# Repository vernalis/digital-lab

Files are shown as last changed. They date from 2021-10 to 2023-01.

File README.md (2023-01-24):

# Vernalis Digital Lab

This repository contains programs for controlling laboratory operations and collecting experimental data. Published by [Vernalis Research][vr].

## Logging Thermocouple

A Raspberry Pi based thermocouple that logs datapoints to a csv file.

[Full Details][thermo]

## Inline Detector

A Raspberry Pi based inline detector, using an Adafruit AS7341 sensor. Allowing detection of slugs within a flow chemistry system, through differing visible light absorbance.

[Full Details][inline]

[vr]: https://www.vernalis.com/
[thermo]: Logging%20Thermocouple
[inline]: Inline%20Detector

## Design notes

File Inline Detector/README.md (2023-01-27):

# Raspberry Pi / Adafruit AS7341 Based Inline Detector

[][paper]


## Overview

A Raspberry Pi based inline detector, using an Adafruit AS7341 sensor. Allowing detection of slugs within a flow chemistry system, through differing visible light absorbance.

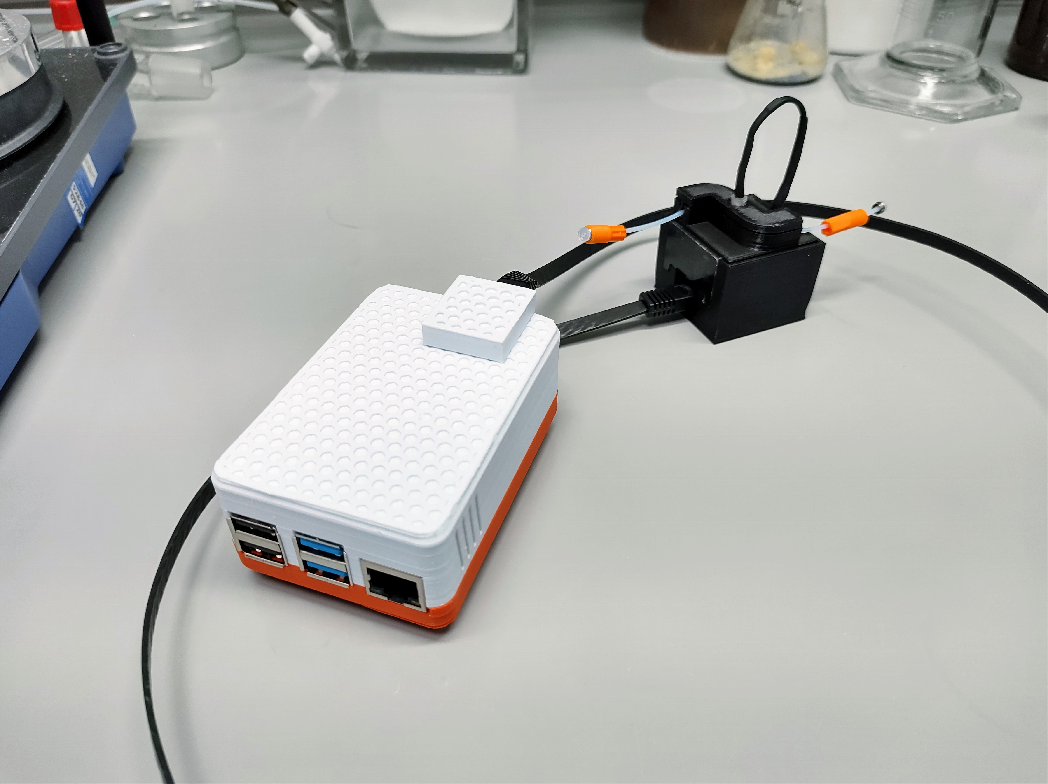
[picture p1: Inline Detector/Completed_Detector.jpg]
Pi_Detector
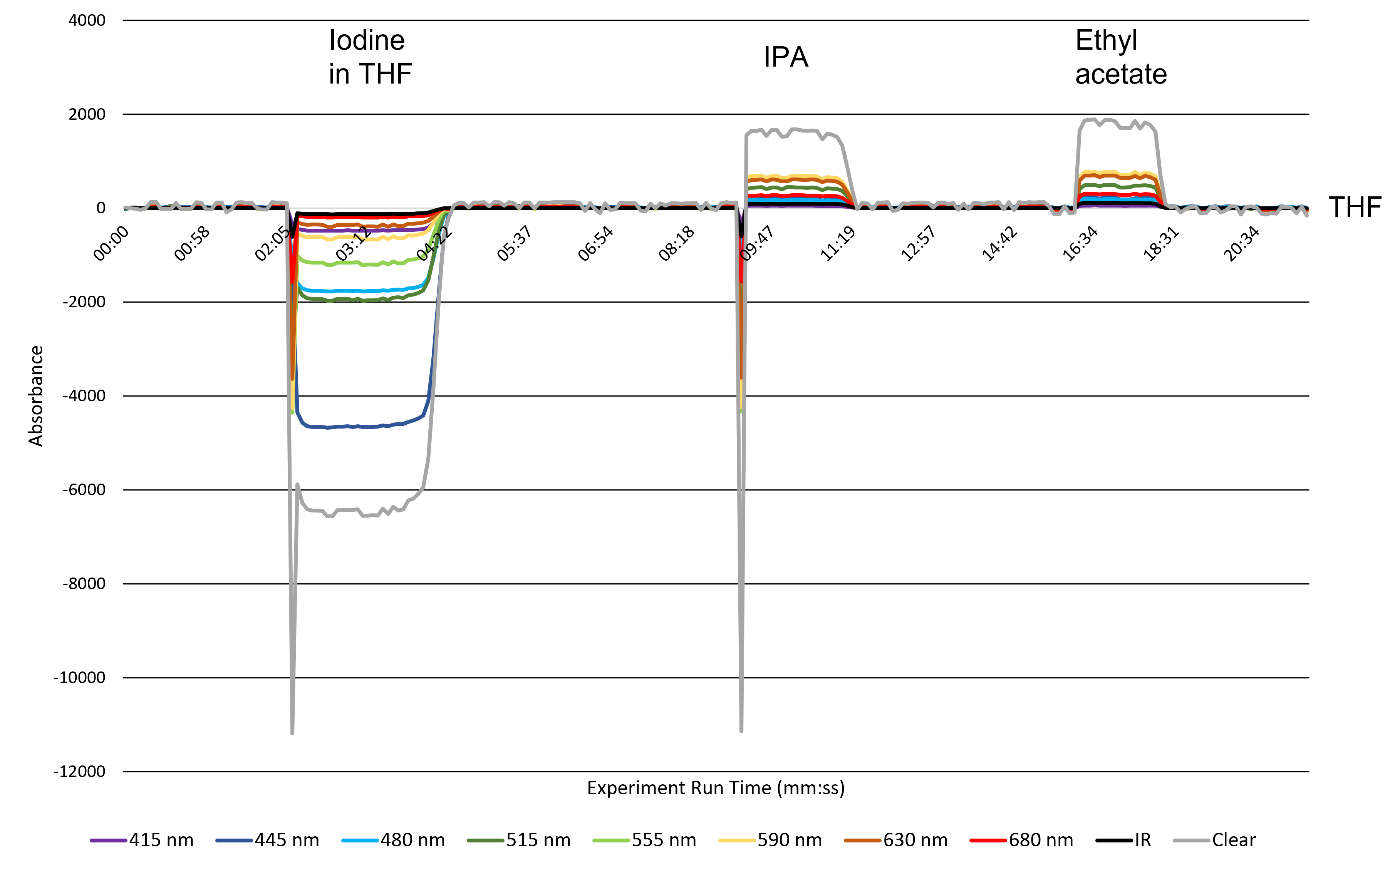
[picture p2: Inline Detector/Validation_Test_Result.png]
Graph_Output
|||
| --- | --- |
|The completed device - Raspberry Pi and detector shown|Graphical output from the detector|

[overview_img]: Completed_Detector.jpg
[graph_img]: Validation_Test_Result.png

## Publication

Details about the design and development of the device can be found in the accompanying paper. A step-by-step guide to building your own is given in the supplementary information.

[Paper][Paper] | [Supplementary Information][si]

If you have used this project as a resource in your research, please cite:

>Maddox D, Davidson JEP, Guetzoyan L, Walmsley L. Development of a Low-Cost Multi-Wavelength Inline Detector for Slug Detection in Continuous Flow. ChemRxiv. Cambridge: Cambridge Open Engage; 2023;  This content is a preprint and has not been peer-reviewed. DOI: [10.26434/chemrxiv-2023-r52zg][paper]

[paper]: https://doi.org/10.26434/chemrxiv-2023-r52zg
[si]: https://chemrxiv.org/engage/api-gateway/chemrxiv/assets/orp/resource/item/63d144546bc5cab0271aab7a/original/supplementary-information.pdf

## Bill of Materials

The following components are required to construct our design. The supplier we used is provided, however parts should be available from alternative suppliers too.

| Name | Catalogue Number | Supplier | Quantity | Total Price (£) |
| ------ | ------ | ------ | ------ | ------ |
| Raspberry Pi 4 Model B | SC0192 | Thepihut.com | 1 | 40.00 |
| 32 Gb MicroSD Card | SD-32GB | Thepihut.com | 1 | 8.00 |
| Adafruit AS7341 10-Channel Light / Color Sensor Breakout (STEMMA QT / Qwiic) | ADA4698 | Thepihut.com | 1 | 15.60 |
| 5mm White LED (forward voltage 3.4V, forward current 30mA) | Components within ELEGOO Upgraded Electronics Fun Kit (ASIN: B01LZRV539) | Amazon.co.uk | 1 | 16.99 |
| NPN Transistor (PN2222) |Components within ELEGOO Upgraded Electronics Fun Kit (ASIN: B01LZRV539)| Amazon.co.uk | 1 | N/A |
| 10 kΩ Resistor |Components within ELEGOO Upgraded Electronics Fun Kit (ASIN: B01LZRV539)| Amazon.co.uk | 2 | N/A |
| 1 kΩ Resistor |Components within ELEGOO Upgraded Electronics Fun Kit (ASIN: B01LZRV539)| Amazon.co.uk | 1 | N/A |
| Sparkfun RJ45 8-Pin Connector | PRT-00643 | Pimoroni.com | 2 | 3.00 |
| Sparkfun RJ45 Breakout | BOB-00716 | Pimoroni.com | 2 | 2.40 |
| 2x20 pin Female GPIO Header for Raspberry Pi| COM0001 |Pimoroni.com | 1 | 1.50 |
| Custom PCB for detector module (price for minimum order of 3 boards shown) | HRKGEPJB (<https://aisler.net/p/HRKGEPJB>) | Aisler.net | 1 | 6.17 |
| Custom PCB for Raspberry Pi HAT (price for minimum order of 3 boards shown) | QVZTMZVR (<https://aisler.net/p/QVZTMZVR>) | Aisler.net |1 | 7.55 |
| PLA Filament for detector module | 832-0264 | uk.rs-online.com/web | 2.7 p/g (prorated price), 37 g used | 1.00 |
| PP Filament for Raspberry Pi case feet | 174-0057 | uk.rs-online.com/web | 5.6 p/g (prorated price), 1 g used | 0.06 |
| PETG Filament for Raspberry Pi case | 190-1962 | uk.rs-online.com/web | 3.5 p/g (prorated price), 53 g used | 1.86 |
| Low profile (flat) LAN cable, 1m | Widely available, e.g. ASIN: B0B6WC6MRB | Amazon.co.uk | 1 | 2.00 |
| 1/16th inch o/d PTFE tubing, with ¼-28” connection at either end | Various suppliers | Various suppliers | Approx. 15cm required | Cost negligible |
|||| Combined Total | £106.13 |

## Repository Contents

This repository contains the following assets to enable reproduction of the device:

* **Original publication** - full documentation for the device is provided within the paper and supplementary information
* **3D Printed Parts** - .stl files for both the detector and Raspberry Pi housing
* **PCB Gerber Files** - to allow manufacture of custom PCBs with alternative suppliers
* **Code** - Python code used to operate the device (inline_detector.py) and a bash script to automate initial configuration (setup-script.sh)

### 3D Printer .stl Files

Files are separated into two folders - components for the Raspberry Pi case, and components for the detector housing.

The Raspberry Pi case is a modified version of [a publicly available Raspberry Pi 4 case](https://www.thingiverse.com/thing:3723561), modified to accommodate the custom HAT designed for this project.  

All Pi case components were printed in PETG due to the higher thermal tolerance, apart from the legs - which were printed in PP due to the higher solvent resistance.

The detector housing parts were all printed in PLA. Take care to print interlocking parts in the same orientation on the print bed to ensure a good fit.

See Supplementary Information section S4 for further details, such as printer settings.

### PCB Gerber Files

Zipped Gerber files are provided to allow manufacture of the custom PCBs at a supplier of your choice.

Alternatively, for convenience, use the following links to use the same supplier as we did. After registration, simply import the designs into your sandbox and order. A minimum order quantity of 3 is required, however the price is minimal.

[HAT PCB](https://aisler.net/p/QVZTMZVR)

[Detector PCB](https://aisler.net/p/HRKGEPJB)

See Supplementary Information section S3 for further details on circuit design. See Supplementary Information section S5 for PCB assembly.

**Note:** The HAT PCB available at publication has undergone a minor revision to the board shown in the publication. This revision decreases the board size by ~1.5mm, allowing compatibility with the Raspberry Pi Zero platform.

### Raspberry Pi Configuration and Operation

#### Configuration

A Raspberry Pi running Raspberry Pi OS Bullseye was used in combination with the following python libraries:

* CircuitPython (Blinka) by Adafruit for interfacing with their products
* adafruit-circuitpython-as7341 for the sensor device itself
* matplotlib for graphical representation of the sensor data
* pandas for data processing

The device was interfaced with predominantly via VNC to allow a familiar GUI experience.

Use the following commands in the Raspberry Pi terminal to download and run an automated configuration script to install all required libraries and the inline detector code itself in one simple process.

~~~bash
wget https://raw.githubusercontent.com/vernalis/digital-lab/main/Inline%20Detector/Code/setup-script.sh
chmod u+x setup-script.sh
./setup-script.sh
~~~

See Supplementary Information section S6.1 for a full step-by-step guide to the configuration process.

#### Operation

Once configured, operating the Raspberry Pi through VNC to allow a graphical interface, initiate the code by opening a terminal window and enter the command:

~~~bash
python inline_detector.py
~~~

After 3 initial baseline readings a graphical output of the sensor data is shown. This then updates every 2.5s with the next datapoint. Data is saved in a .csv file at each update.

At the end of the experiment, closing the window will terminate the code, saving a .png of the graph to the same folder as the .csv files.

See Supplementary Information section S6.2 for full details.

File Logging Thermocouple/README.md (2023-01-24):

# Raspberry Pi Based Logging Thermocouple

[][paper]


## Publication

Detailed information about the design and testing of these files is available in the accompanying paper:

[Paper][paper] | [Supplementary Information][si]

If you have used this project as a resource in your research, please cite:

> David Lee Walmsley, Stephen Hilton, Emilie Sellier, Matthew Penny, Daniel Maddox (2021) “Control and Monitoring of Temperature in 3D-Printed Circular Disk Reactors for Continuous Flow Photochemistry using Raspberry Pi Based Software” ChemRxiv. DOI: [10.33774/chemrxiv-2021-cxs25][paper]

[paper]: https://doi.org/10.33774/chemrxiv-2021-cxs25
[si]: https://chemrxiv.org/engage/api-gateway/chemrxiv/assets/orp/resource/item/617fc58581c4fc77f2e8b692/original/control-and-monitoring-of-temperature-in-3d-printed-circular-disk-reactors-for-continuous-flow-photochemistry-using-raspberry-pi-based-software.pdf

## Assembly Instructions

### Bill Of Materials

| Description | Product Number | Source | Price (£) |
| ------ | ------ | ------ | ------ |
| Raspberry Pi 4 Model B 2Gb | SC0193 | thepihut.com | 33.90 |
| Official UK Raspberry Pi 4 Power Supply (5.1V 3A) | SC0212 | thepihut.com | 7.50 |
| Raspbian Preinstalled 16GB Micro SD Card [Discontinued] | SC0267 | thepihut.com | 8.00 |
| Thermocouple Amplifier MAX31855 breakout board | ADA269 | thepihut.com | 13.00 |
| Thermocouple Type-K Glass Braid Insulated Stainless Steel Tip | ADA3245 | thepihut.com | 8.70 |
| RGB LCD Shield Kit w/ 16x2 Character Display | ADA716 | thepihut.com | 20.80 |
| 3D Printing Filament Made in Germany 1.75 mm 2.85 mm PLA PETG HIPS 15 Colours 1 kg Spool or Refill | 8719689844059 | amazon.co.uk | (24.88/ kg, 71 g used) 1.77 |
| **Total** |  |  | **(116.78) 93.67** |

A modified version of [a publicly available Raspberry Pi 4 case](https://www.thingiverse.com/thing:3723561) was designed to accommodate RGB LCD shield (ADA716) – allowing headless operation of the device and containment of all components. STL files and further instructions for this modified case are available in the [Vernalis 3D-printing Files Repository][case]. This was printed in PETG filament to provide good temperature resilience during operation even during high CPU usage.

[case]: https://github.com/vernalis/3Dprint_files

### Assembly

Raspberry Pi 4 containing 16Gb SD card (with operating system pre-installed) was fitted into the base of the case.

Thermocouple amplifier (ADA269) interfaces using SPI and was connected to 3V (Vin), Ground (Gnd), GPIO 9 (Do/MISO), GPIO 11 (Clk) and GPIO 5 (CS). Type-K class thermocouple (ADA3245) was connected to positive and negative terminals, noting correct polarity [ref][ADA269]. Thermocouple threaded through side port included in upper portion of case.

RGB LCD Shield (ADA716) was constructed according to supplier instructions [[ref][ADA716]]. The screen and buttons primarily interface using I2C, with the reset button operating as an independent switch monitored on a separate GPIO pin. Shield was connected to 5V, Ground, GPIO 2 (Data/SDA), GPIO 3 (Clock/SCL) and GPIO 17 (Reset, configured pin to be ‘pull up’). Screen was then mounted into upper portion of case using 4 screws (M2.5 nuts printed into the casing). Case could then be snapped together closed.

Fritzing and circuit diagrams follow below:

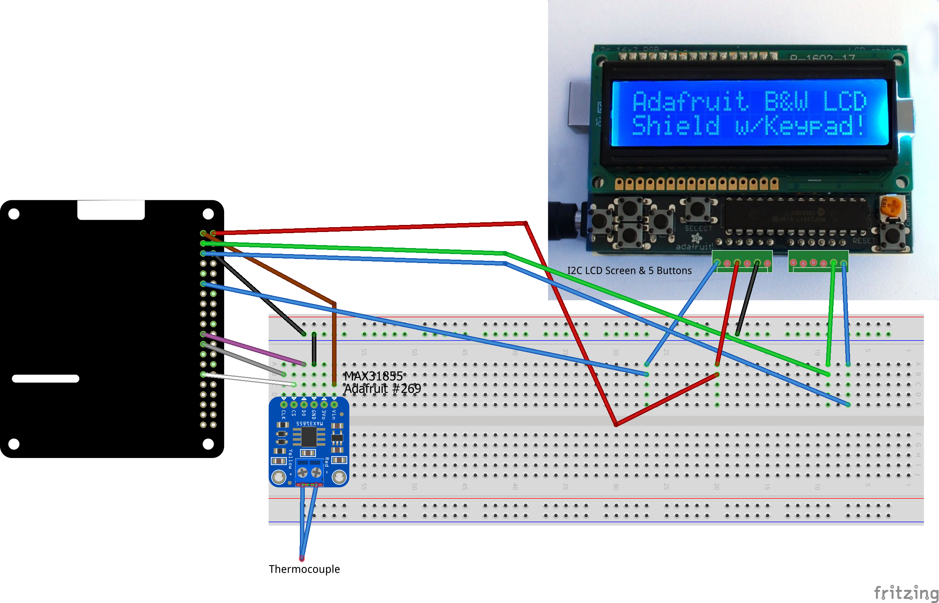
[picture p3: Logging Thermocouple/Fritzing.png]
Fritzing_Diagram


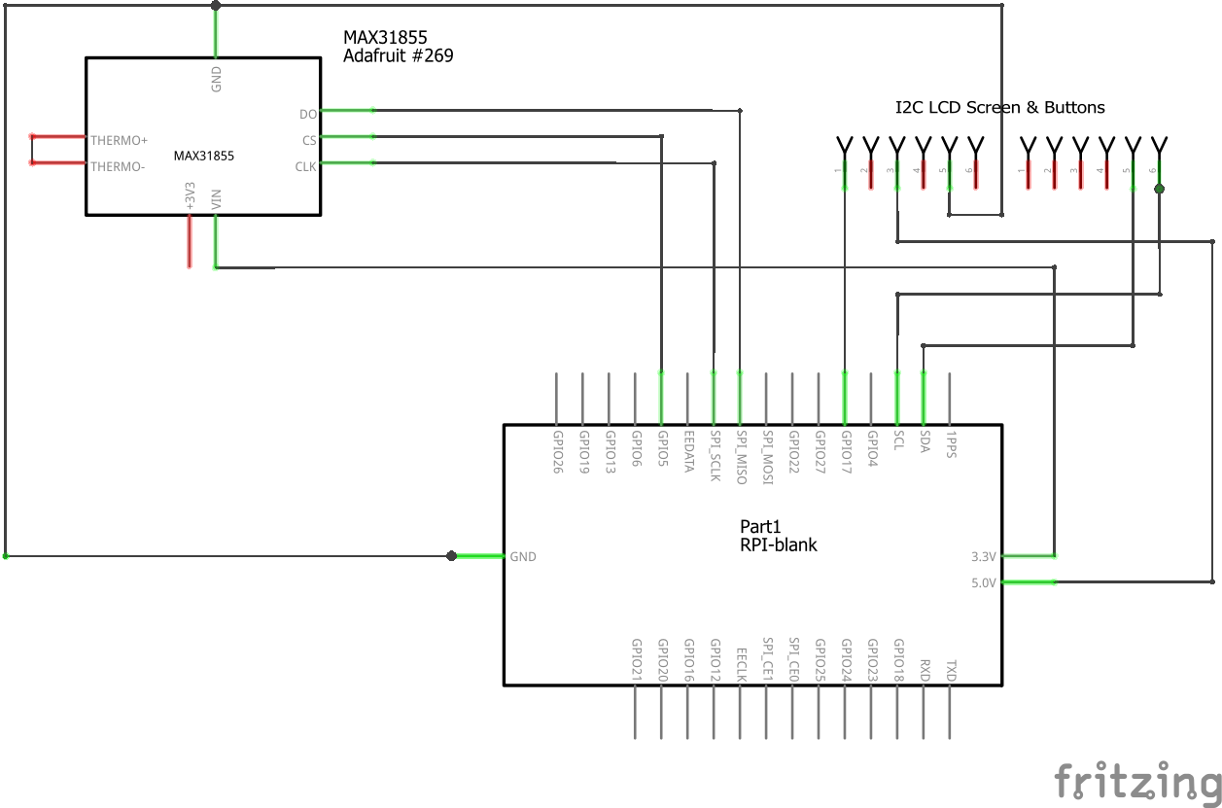
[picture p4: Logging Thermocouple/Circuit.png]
Circuit_Diagram


[circuit]: Circuit.png
[fritzing]: Fritzing.png
[ADA269]: https://learn.adafruit.com/thermocouple/overview
[ADA716]: https://learn.adafruit.com/rgb-lcd-shield/overview

## Code & Usage

Datalogging code written and tested in Python 3.7.3 using Thonny IDE. Thermocouple interface code based on that supplied by manufacturer [[ref][ADA269]]. Screen I2C interface code based on that supplied by manufacturer [[ref][ADA716]].

By default the script will output a CSV to the user folder, however can also be configured to output to a defined location by either of two methods. First, by providing the path as a command line argument:

```bash
python logging_thermocouple.py /path/to/output/folder/
```

Or secondly by setting an environment variable:

```bash
export VER_THERM_LOG=/path/to/output/folder
python logging_thermocouple.py
```

Once started, the code will log a temperature every 15 seconds to a csv file in a pre-defined file location and update the LCD screen accordingly.
To prevent log file corruption, press and hold the reset button to ‘break’ and stop the code loop.

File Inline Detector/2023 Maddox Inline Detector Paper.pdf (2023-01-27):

## Development of a Low-Cost Multi-Wavelength Inline Detector for Slug Detection in Continuous Flow

Daniel Maddox†*, James E. P. Davidson†, Lucie Guetzoyan† and Lee Walmsley†

†Vernalis Research, Granta Park, Great Abington, Cambridge, Cambridgeshire CB21 6GB, UK

Herein we describe our expansion upon previously published low-cost inline detectors. Using an Adafruit AS7341 10-channel light/colour sensor, a Raspberry Pi, and a white LED we were able to simultaneously monitor infrared and multiple visible spectrum absorption wavelengths. This allowed even challenging colourless slugs within a colourless carrier solvent to be detected and characterised as they progressed through a flow reactor. The sensor data is displayed in graphical form in real-time and stored on the device for reference afterwards.

In this publication we provide details on the design and development of a Raspberry Pi based, low-cost inline detector suitable for use with flow chemistry systems (Figure 1).

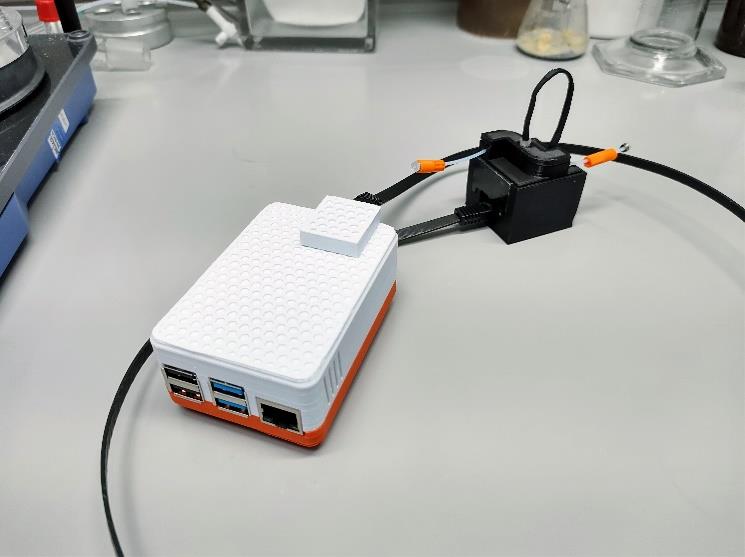
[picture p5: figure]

Flow chemistry enables reactions to be performed as a continuous process with precise control of reaction conditions such as temperature, pressure, and stoichiometry. [1]
Flow reactions can be performed in two regimes – continuous or slug flow. In continuous flow the entire fluidic system is filled with reagents, intermediate or formed product. Conversely in slug flow much of the fluidic system is filled with carrier solvent, small discrete reaction slugs then flow through the system (Figure 2, A). Although slug flow reactions are being performed on a much smaller reaction scale, on a microfluidic scale the same reaction is performed. This means at identical positions within the flow reactor an identical profile is observed in both the slug and continuous flow regime. This linear scalability makes slug flow chemistry ideal for library synthesis in flow.

Two critical considerations when performing slug flow chemistry is the timing and profile of the slug. Knowing to a high degree of accuracy where a reaction slug is within a fluidic system that is likely 10 or more times the volume of the reaction slug is crucial to enable effective collection of the product solution. This becomes even more apparent when two reactant slugs need to meet at a t-mixer. For a complete reaction, both slugs need to begin and end with perfect synchronicity (Figure 2, B) – where the two slugs do not overlap one reagent does not see the other, meaning no reaction can occur (Figure 2, C).

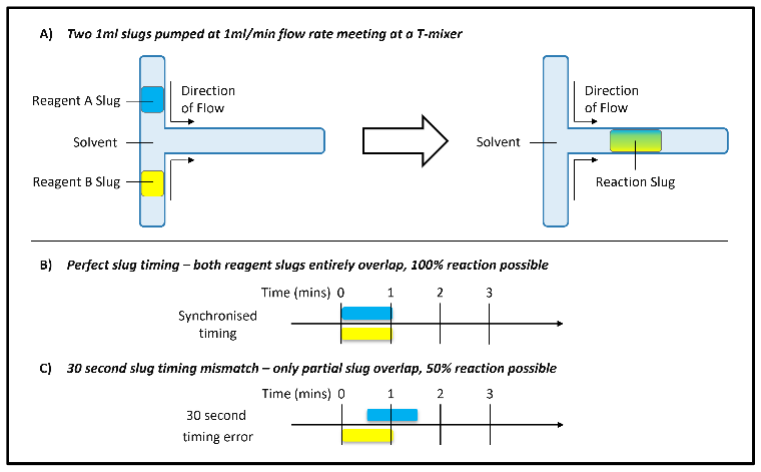
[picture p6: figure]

Prediction of slug timing within a simple tubular flow reactor can be achieved when both the flow rate and system volume are known to a high degree of accuracy, so long as the flow rate is well controlled. In more complex fluidic systems however – in particular when a solid phase reactor is present – prediction of slug timing can become more difficult to predict due to the chromatographic effect of the stationary phase reaction surface. [2]

Figure 2 - A) Representation of two reagent slugs meeting at a T-mixer. B & C) The importance of slug timing

Figure 1 - Our completed design - a low cost detector module connected to a Raspberry Pi computer

If reaction slugs are highly coloured, and see-through PTFE/PFA or similar material tubing is used then slug timing can be corroborated by eye. If either of these factors is not the case however, then inline detection is required to ‘see’ the reaction slug. Several inline detection technologies are commercially available including inline flow NMR, MS, IR or UV.

[3 - 4] All of
these commercial examples however are significantly priced and have a sizeable footprint to accommodate within a fume cupboard that likely already contains a large amount of equipment associated with the flow reactor itself. As a result, multiple groups have reported their efforts to overcome these issues, creating low-cost inline detectors relying on the absorbance of visible spectrum light. [5 - 6]

Whilst elegant and likely to generate high quality and sensitive data thanks to the reference measurement being taken, the resultant complex optical setup using a beam-splitter cube and optical fibres of the detector published by Glotz & Kappe [5] makes replication of
the | literature | challenging | without | sufficient
engineering expertise.

The later publication from Höving et al.

[6] was the
basis of a much simpler design. In the Höving et al. publication, the flow reactor tube was sandwiched between a coloured LED (Light Emitting Diode) and LDR (Light Dependent Resistor) and held together in a specially designed 3D printed housing. The simplicity of this design made it a much more tangible prospect for us to be able to reproduce. The reliance of the design however, on a single wavelength LED, and typically low sensitivity LDR, made us question if further enhancements could be made to increase the applicability.

With the rise of single board computers such as the Raspberry Pi and Arduino Uno a market has emerged for a wide range of sensors that can easily be incorporated into these systems. For this application, the Adafruit AS7341 sensor looked ideal. [7] The sensor measures light across 10 wavelength ‘channels’ (IR, 8 visible spectrum wavelengths, and a ‘clear’ channel that covers that entire spectrum) and can be interfaced with easily using I

2C (Inter-Integrated
Circuit). If a white LED was used to irradiate the reactor pipe, then the absorbance of the fluid within the pipe could be determined at multiple wavelengths simultaneously – providing richer data than the previously published inline detectors at a similar low cost.

Measuring absorbance across a wide range of wavelengths would also negate the need to optimise the detector for the substrate you wish to measure. Comparing the absorbance ‘fingerprints’ of two apparently colourless substances could enable easy identification of colourless slugs within a colourless carrier solvent.

Design and Development

Using the “Version B” flow cell design from the Höving et al. publication [6] as a starting point, an initial prototype detector housing was designed in Tinkercad.[8] Although only 2.6 x 1.8 cm in size, the Adafruit AS7341 sensor board is significantly larger than an LDR as used in the previous publication. As a result, modifications were required to encase the

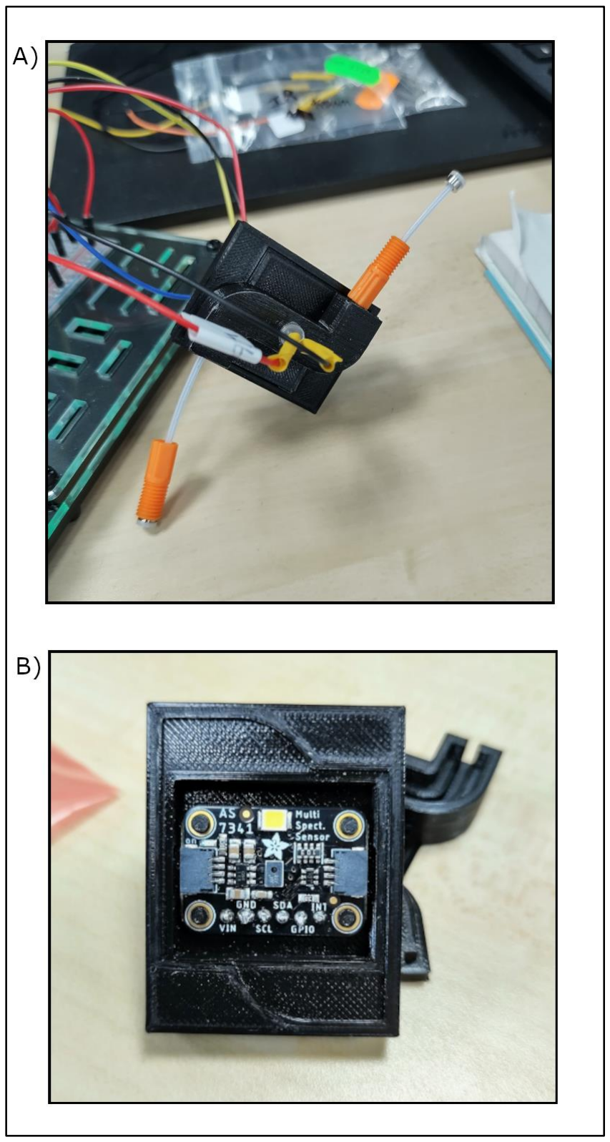
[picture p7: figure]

Figure 3 - A) Assembled prototype inline detector B) Sensor within prototype detector module

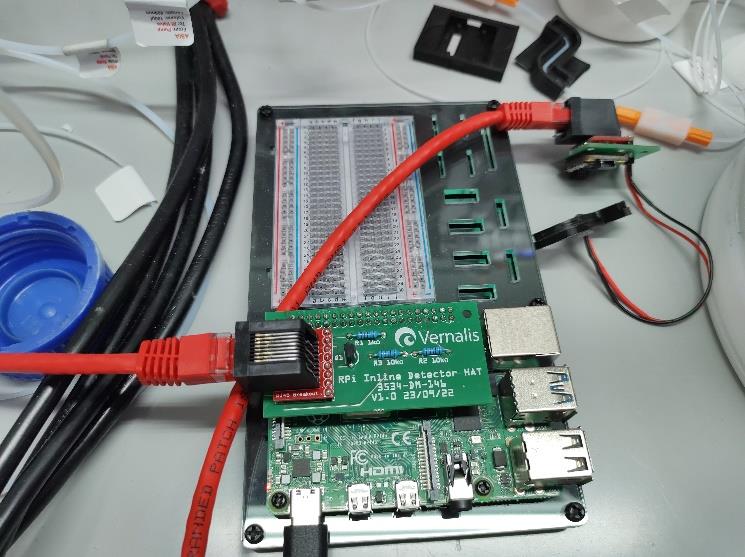
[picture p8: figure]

larger Adafruit AS7341 sensor board to create a light-proof box, whilst exposing the sensor pins to allow circuit prototyping with the Raspberry Pi and a breadboard (Figure 3).

To complete the prototype device a white LED was also controlled by the Raspberry Pi, using PWM (Pulse Width Modulation) to optionally control brightness of the LED, allowing the effect of varying irradiation brightness to be tested.

Initial experiments using this prototype device confirmed our hopes. Using the example code provided by Adafruit [7] and pumping test solutions through the flow cell using a hand operated syringe; THF, IPA (isopropyl alcohol) and ethyl acetate showed differences in absorbance, despite all being colourless liquids to the human eye.

To transform the prototype into a useable device that could be housed and operated in a laboratory fume cupboard two major improvements needed to be made: the fragile breadboard prototype circuitry needed to be rigidified and then protected from potential solvent splashes etc, and a better representation of the sensor data also needed to be created rather than using the Adafruit example code.

To consolidate and rigidify the circuitry bespoke printed circuit boards were designed using circuit design software tool Fritzing and then fabricated at a low volume PCB manufacturer, Aisler. A design strategy commonly employed in the single board computer arena was used – a Pi HAT (Hardware Attached on Top) circuit board was designed to contain all the control electronics in an easily attachable/detachable board. A second smaller circuit board was designed for the detector and LED.

On both boards was also included an RJ45 (ethernet) port. An ethernet cable was chosen to consolidate the 6 wires required to power the LED and communicate with the sensor into a single cable (leaving two of the eight wires unused). The choice was made to use a ubiquitous, easily interchangeable cable so that any cable of suitable length could be selected as required dependent on location. This design then allows the detector and Raspberry Pi to be located any distance apart by simply choosing a longer or shorter ethernet cable (Figure 4).

The initial proof-of-concept code supplied by Adafruit displays the sensor wavelength readings in a histogram form, refreshing each time sensor values are read. To allow us to see changes in absorption over time, and thus identify when slugs are passing the detector, the data needed to be represented as a line graph – plotting sensor readings versus time (Figure 6). This was achieved using the python programming language: using the “pandas” module for tabular data storage and “matplotlib” to output the data in a graphical form. In addition to displaying the plot in real-time, the tabulated data as a .csv file and a .png image of the graph are also stored.

Further testing of the device was carried out to determine the best operation protocol. It was found slugs were much easier to visualise graphically if the sensor channel data is baselined to the absorbance of the system solvent (see Supplementary Information, Figure S20). This then results in a clear positive or negative peak in the trace when a slug is passing the detector. LED brightness was also tested, and full power was found to give the best signal to noise ratio (the LED is not too bright to cause saturation of the detector).

Finally, we needed to provide a secure and protective housing for the new detector circuit board and separately the Raspberry Pi computer. The initial prototype 3D printed sensor housing was modified further to accommodate the RJ45 connector now included. The sensor device is an approximately 4.5 x 4.5 x 4.5 cm cube – still a very small footprint and thus very portable, allowing positioning wherever required in a fluidic system (Figure 5). For the Raspberry Pi

Figure 4 - Custom circuit boards consolidate device electronics, using an ethernet cable to connect the sensor board to the Raspberry Pi HAT

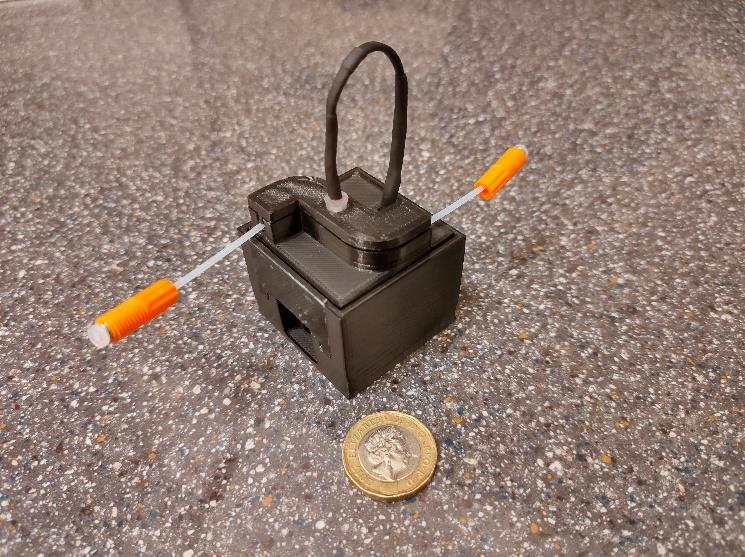
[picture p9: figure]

housing, a suitable case available on the Thingiverse was chosen. [9] Minor modifications were made to accommodate the RJ45 connector we introduced, which stands taller than most Pi HAT devices.

With construction of the final design complete we carried out a more thorough validation test using our Syrris Asia flow chemistry system. Running THF as the system solvent we injected sequential slugs of dilute iodine in THF (as a coloured, positive control) followed by IPA and then ethyl acetate. All slugs could be clearly visualised as distinctly different to the THF system solvent – confirming the device works as anticipated (Figure 6).

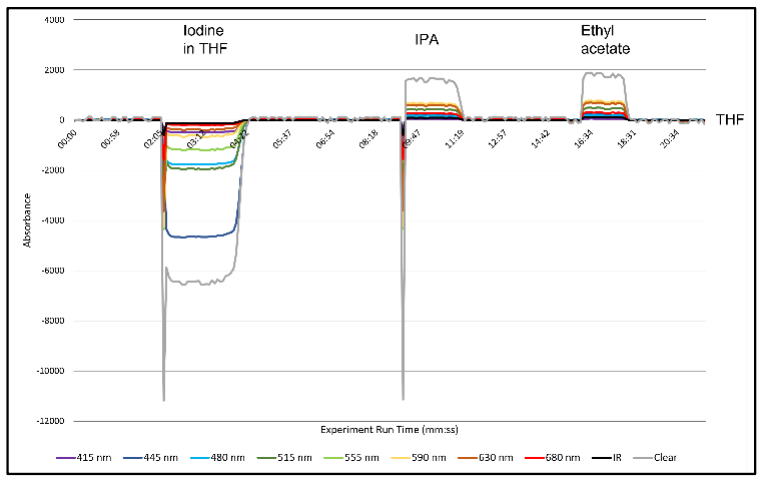
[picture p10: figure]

Conclusion

In conclusion, in this publication we report a significant enhancement on the previously published low-cost inline detector from Höving et al. [6] by changing the detector to one that can measure multiple wavelengths simultaneously and changing the irradiation source to a white LED. As a result, we were able to obtain real-time inline spectral data from a flow reactor operating in a slug flow regime, indicating when slugs pass the detector even when undetectable to the human eye.

This device enables slug timing within a flow reactor to be determined in a quick and facile manner. Furthermore, the device could be used to monitor residence time distribution within a system based on shape of the slug peak, along with perhaps estimation of reaction conversion if the optical absorbance profile of starting material and product were known.

Details to construct the device are provided in the supplementary information document, including links to purchase the printed circuit boards directly from the manufacturer we used. Source code, 3D print .stl files and circuit board Gerber files (if you wish to organise manufacture yourself) are all provided on our GitHub repository:

https://github.com/vernalis/digital-lab/tree/main/Inline%20Detector (https://github.com/vernalis/digital-lab/tree/main/Inline%20Detector)

References

[1] Plutschack, M. B. et al. The Hitchhiker’s guide to flow chemistry. Chem. Rev., 2017, 117, 11796-11893.
https://doi.org/10.1021/acs.chemrev.7b0018 3 (https://doi.org/10.1021/acs.chemrev.7b00183)
[2] Abdiaj, I. et al. End-to-end automated synthesis of C(sp³
)-enriched drug-like
molecules via Negishi coupling and novel, automated liquid-liquid extraction. J. Med. Chem.¸2023, 66, 1, 716-732. https://doi.org/10.1021/acs.jmedchem.2c016 46 (https://doi.org/10.1021/acs.jmedchem.2c01646)
[3] Rodriguez-Zubiri, M. & Felpin, F.-X. Analytical tools integrated in continuous-flow reactors: which one for what? Org. Process Res. Dev., 2022, 26, 6, 1766-1793.
https://pubs.acs.org/doi/10.1021/acs.oprd.2c 00102 (https://pubs.acs.org/doi/10.1021/acs.oprd.2c00102)
[4] https://www.uniqsis.com/paProductsDetail.aspx?ID=Flow-UV (https://www.uniqsis.com/paProductsDetail.aspx?ID=Flow-UV)
[5] Glotz, G. & Kappe, C. O. Design and construction of an open source-based photometer and its applications in flow chemistry. React. Chem. Eng., 2018, 3, 478-
486. https://doi.org/10.1039/C8RE00070K

Figure 5 - The finalised detector module. £1 coin for scale

Figure 6 - Graphical output from detector - slugs are clearly detectable versus THF baseline

[6] Höving, S., Bobers, J. & Kockmann, N. Open-source multi-purpose sensor for measurements in continuous capillary flow. J Flow Chem 12, 185–196 (2022). https://doi.org/10.1007/s41981-021-00214-w
[7] https://learn.adafruit.com/adafruit-as7341-10-channel-light-color-sensor-breakout/ (https://learn.adafruit.com/adafruit-as7341-10-channel-light-color-sensor-breakout/)
[8] https://www.tinkercad.com/3d-design
[9] https://www.thingiverse.com/thing:3723561

[*] Corresponding Author
Daniel Maddox
Vernalis Research,
Granta Park,
Great Abington,
Cambridge,
CB21 6GB
e-mail: d.maddox@vernalis.com

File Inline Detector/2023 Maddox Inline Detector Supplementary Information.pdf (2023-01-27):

# Supplementary Information

# Development of a Low-Cost Multi-Wavelength Inline Detector for Slug Detection in Continuous Flow

Daniel Maddox†*, James E. P. Davidson†, Lucie Guetzoyan† and Lee Walmsley†

†Vernalis Research, Granta Park, Great Abington, Cambridge, Cambridgeshire CB21 6GB, UK

[*] Corresponding Author
Daniel Maddox
Vernalis Research,
Granta Park,
Great Abington,
Cambridge,
CB21 6GB
e-mail: d.maddox@vernalis.com

S2

## Table of Contents

S1 - General Considerations | S3
S2 - Bill of Materials | S4
S3 - Circuit Design | S5
S3.1 - Prototype Circuit Design | S6
S3.2 - Finalised Circuit Design | S7
S3.3 - Custom Circuit Board Availability | S9
S4 - Design of 3D Printed Housings | S10
S4.1 - Detector Module Design | S10
S4.2 - Raspberry Pi Case Design | S13
S4.3 - STL File Availability | S14
S4.4 - 3D Printing Settings | S14
S5 - Assembly of Devices | S15
S5.1 - Assembly of Detector Module Circuit Board | S15
S5.2 - Assembly of Detector Module | S17
S5.3 - Assembly of HAT Circuit Board | S19
S5.4 - Assembly of Raspberry Pi Module | S20
S6 - Raspberry Pi Configuration and Operation | S21
S6.1 - Configuring Raspberry Pi for Use | S21
S6.2 - Inline Detector Operation | S22
S7 - Testing | S23
S7.1 - Initial Optimisation | S23
S7.2 - Validation of Detector | S24
S8 - References | S25

## S1 - General Considerations

Herein we provide full details of the design, assembly, and use of our inline detector.

The design consists of two major components: the detector module which houses the detector, fluidic piping (acting as the flow cell), a white LED and a RJ45 connector; and a Raspberry Pi 4 Model B which comprises of a standard Raspberry Pi as well as a custom HAT (Hardware Attached on Top) which contains the control electronics for the LED in addition to a RJ45 connector. The two devices are interconnected using an RJ45 cable. Both devices are housed in custom designed 3D-printed cases. A Raspberry Pi Zero should also be compatible, however the smaller 3D printed case has not been designed, nor has the lesser computational performance been tested.

The detector is operated using the Raspberry Pi, interfacing via a connected screen or remote desktop protocol. The supplied code plots a graph of datapoints from the detector, refreshing upon each new datapoint acquisition. The code also stores the data as a .csv file for review later, along with a .png image of the graph.

All associated files can be found on the Vernalis GitHub: https://github.com/vernalis/digital-lab/tree/main/Inline%20Detector (https://github.com/vernalis/digital-lab/tree/main/Inline%20Detector)

## S2 - Bill of Materials

The following components and materials are required to construct our design:

Item | Catalogue Number | Supplier | Quantity | Total Price (£)
Raspberry Pi 4 Model B | SC0192 | Thepihut.com | 1 | 40.00
32 Gb MicroSD Card | SD-32GB | Thepihut.com | 1 | 8.00
Adafruit AS7341 10-Channel Light / Color Sensor Breakout (STEMMA QT / Qwiic) | ADA4698 | Thepihut.com | 1 | 15.60
5mm White LED (forward voltage 3.4V, forward current 30mA) | Components within ELEGOO Upgraded Electronics Fun Kit ASIN: B01LZRV539 | Amazon.co.uk | 1 | 16.99 NPN Transistor
(PN2222) | | | 1
10 kΩ Resistor | | | 2
1 kΩ Resistor | | | 1
Sparkfun RJ45 8-Pin Connector | PRT-00643 | Pimoroni.com | 2 | 3.00
Sparkfun RJ45 Breakout | BOB-00716 | Pimoroni.com | 2 | 2.40
2x20 pin Female GPIO Header for Raspberry Pi | COM0001 | Pimoroni.com | 1 | 1.50
Custom PCB for detector module (price for minimum order of 3 boards shown) | HRKGEPJB (https://aisler.net/p/HRKGEPJB) | Aisler.net | 1 | 6.17
Custom PCB for Raspberry Pi HAT (price for minimum order of 3 boards shown) | QVZTMZVR (https://aisler.net/p/QVZTMZVR) | Aisler.net | 1 | 7.55
PLA Filament for detector module | 832-0264 | uk.rs-online.com/web | 2.7 p/g (prorated price), 37 g used | 1.00
PP Filament for Raspberry Pi case feet | 174-0057 | uk.rs-online.com/web | 5.6 p/g (prorated price), 1 g used | 0.06

PETG Filament for Raspberry Pi case | 190-1962 | uk.rs-online.com/web | 3.5 p/g (prorated price), 53 g used | 1.86
Low profile (flat) LAN cable, 1m | Widely available, e.g. ASIN: B0B6WC6MRB | Amazon.co.uk | 1 | 2.00
1/16th inch o/d PTFE tubing, with ¼-28” connection at either end | Various suppliers, approx. 15cm required, cost negligible
| | | Combined total | £106.13

Table S1 - Bill of materials

## S3 - Circuit Design

The device consists of two circuits (sensor board and LED), both are powered and controlled by the Raspberry Pi.

The sensor board is powered by 3.3V and communicates with the Pi over I²C (thus using the SDA and SCL pins). The sensor board is therefore connected to GPIO pins 2 (I²C SDA), 3(I²C SCL), a 3v3 and a ground pin.

The high-power white LED has a forward voltage greater than that provided by a standard GPIO pin (3.4V versus 3.3V). As a result, the LED must be powered by a 5V pin (with 1 kΩ resistor) and then controlled by a separate GPIO pin using an NPN transistor (via a 20 kΩ resistor) to complete the circuit. [1] To allow dimming of the LED brightness, the controlling GPIO pin uses PWM (Pulse Width Modulation) [2]
, however in our initial studies we have found 100% brightness (i.e. no PWM) gave the best signal/noise result (see S7.1). The LED circuit is thus connected to GPIO pin 13 (PWM), a 5V and a ground pin.

In the prototype circuit design all circuits were directly connected between the component and the Raspberry Pi. In the finalised design, to allow easy and customisable length of separation between the Raspberry Pi and the detector module, as well as consolidation of 6 wires into one cable, an RJ45 ethernet cable was used. Components are attached to each other via the PCB circuitry, rather than the wires depicted in the original prototype diagram.

For ease of understanding both the prototype and finalised circuits are provided in the following sections, however both are essentially identical.

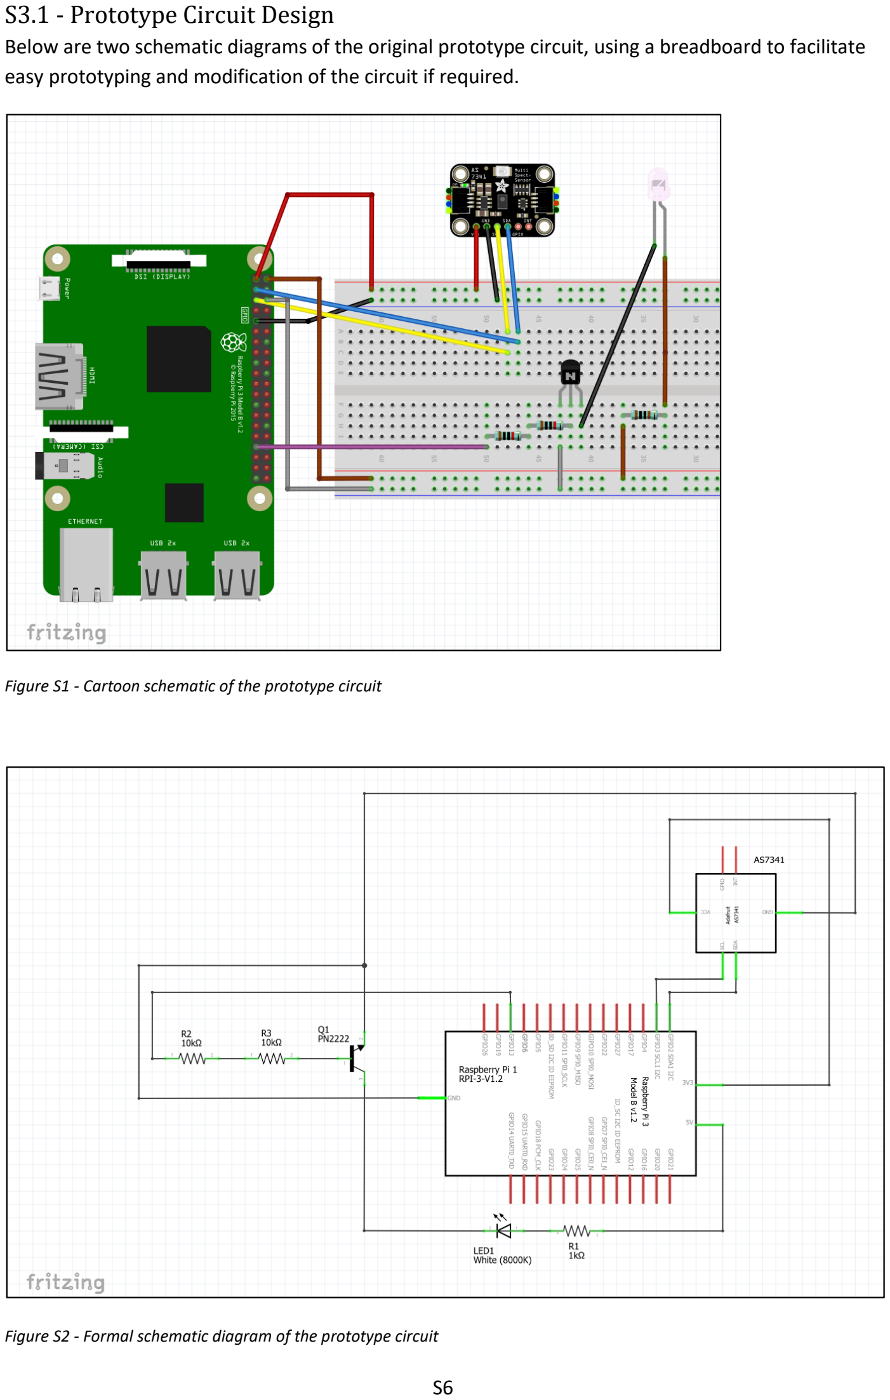
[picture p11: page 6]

### S3.1 - Prototype Circuit Design

Below are two schematic diagrams of the original prototype circuit, using a breadboard to facilitate easy prototyping and modification of the circuit if required.

Figure S1 - Cartoon schematic of the prototype circuit

Figure S2 - Formal schematic diagram of the prototype circuit

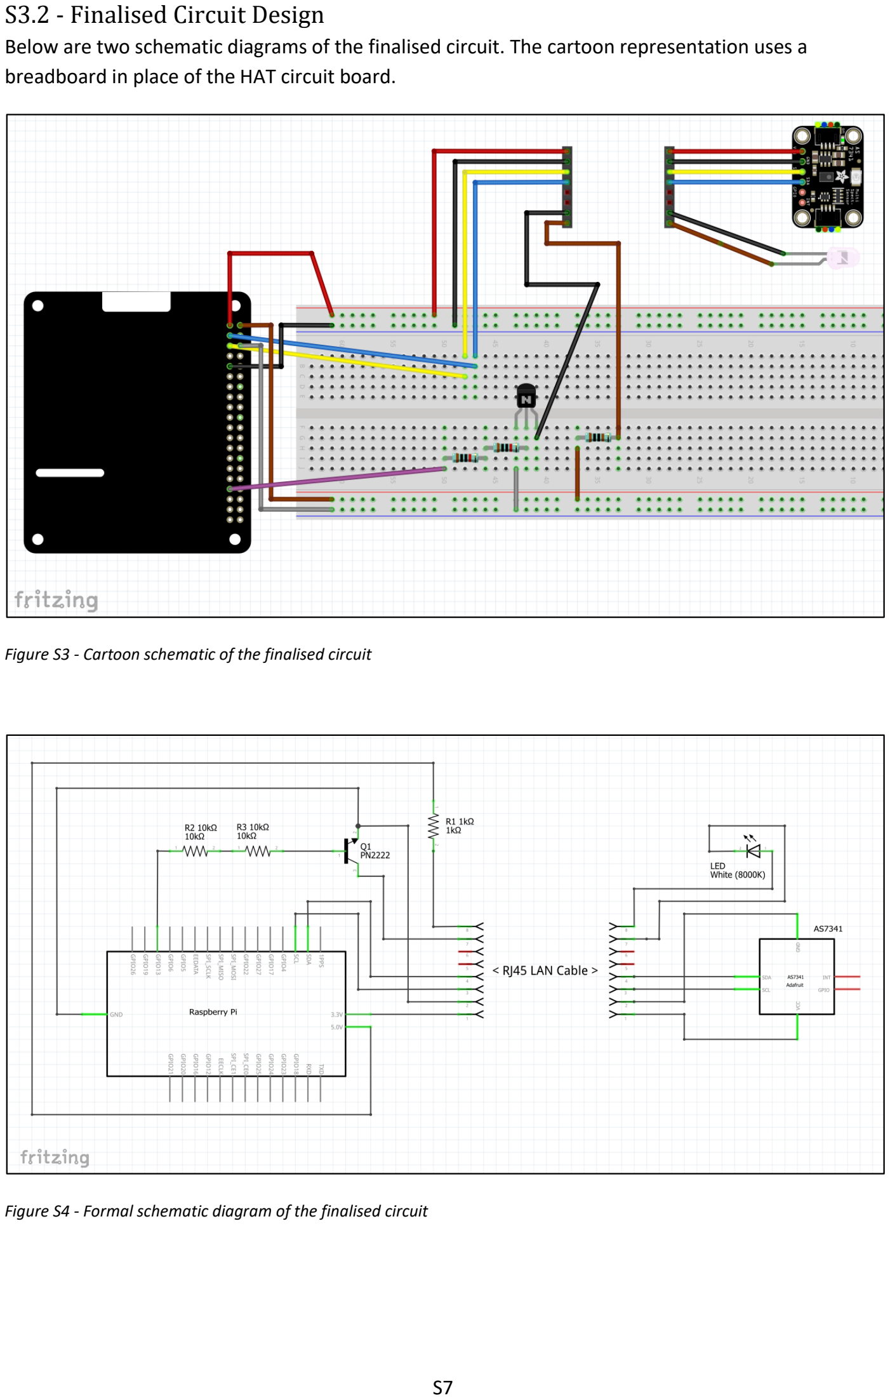
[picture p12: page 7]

### S3.2 - Finalised Circuit Design

Below are two schematic diagrams of the finalised circuit. The cartoon representation uses a breadboard in place of the HAT circuit board.

Figure S3 - Cartoon schematic of the finalised circuit

Figure S4 - Formal schematic diagram of the finalised circuit

Below are the two custom PCB designs. To keep the detector module as small as possible the sensor and LED are on one side of the board, with the RJ45 connector mounted on the underside. A female GPIO socket connector was used to enable easy attachment/detachment of the HAT to the Pi. Note: the two different colours of orange depict the two copper layers within the board. Black markings indicate silkscreen labels on the boards. The HAT is small enough to also fit a Pi Zero.

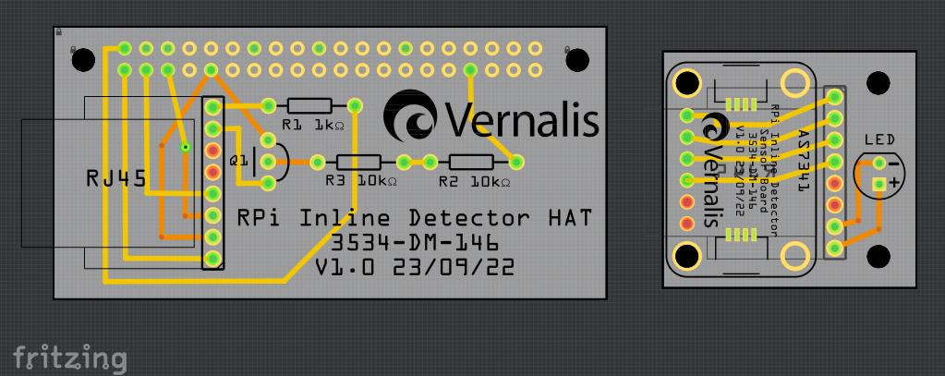
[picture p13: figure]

Figure S5 - Custom PCB designs

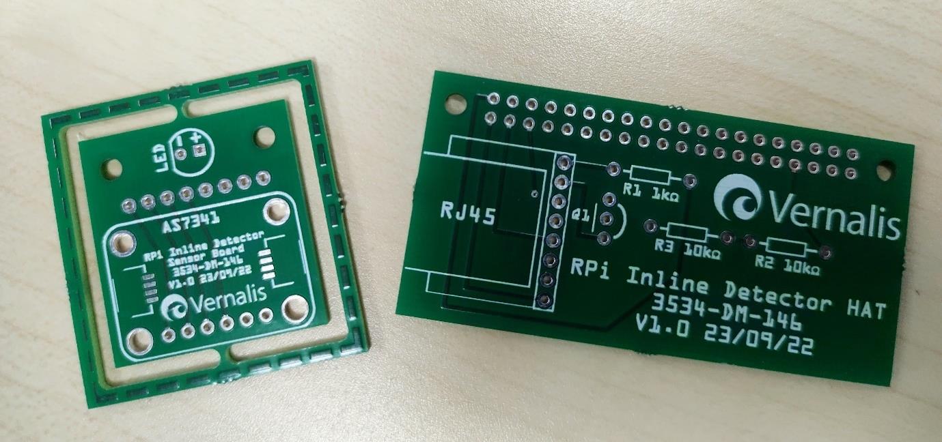
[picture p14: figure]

Figure S6 - Custom PCBs as delivered. Note - smaller detector board has manufacturing excess that requires removal

### S3.3 - Custom Circuit Board Availability

The two custom PCB designs are available to order directly from the manufacturer we used (Aisler). To order the HAT visit https://aisler.net/p/QVZTMZVR , to order the detector module board visit https://aisler.net/p/HRKGEPJB . After registration the designs can then be imported to your account and ordered. A minimum order quantity of 3 is required, however the price is minimal (see Table 1).

Alternatively, the PCB Gerber files have been uploaded to our GitHub page, allowing manufacture elsewhere - https://github.com/vernalis/digital-lab/tree/main/Inline%20Detector/PCB%20Gerber%20Files (https://github.com/vernalis/digital-lab/tree/main/Inline%20Detector/PCB%20Gerber%20Files)

Note: The HAT PCB available at publication has undergone a minor revision to the board shown above. This revision decreases the board size by ~1.5mm, allowing compatibility with the Raspberry Pi Zero platform.

See section S5 for assembly instructions.

## S4 - Design of 3D Printed Housings

All 3D design was carried out using Tinkercad – a free, web-based CAD tool.

### S4.1 - Detector Module Design

The starting point for the detector module design was the previously published “Version B” sensor housing design by Höving et al.. [3] Using the stl for this design and creating a CAD version of the Adafruit AS7341 sensor we were able to design the additional structure required to create a secure, lightproof housing for the larger sensor.

As an initial prototype, we designed a housing to simply encase the sensor (Figure S7).

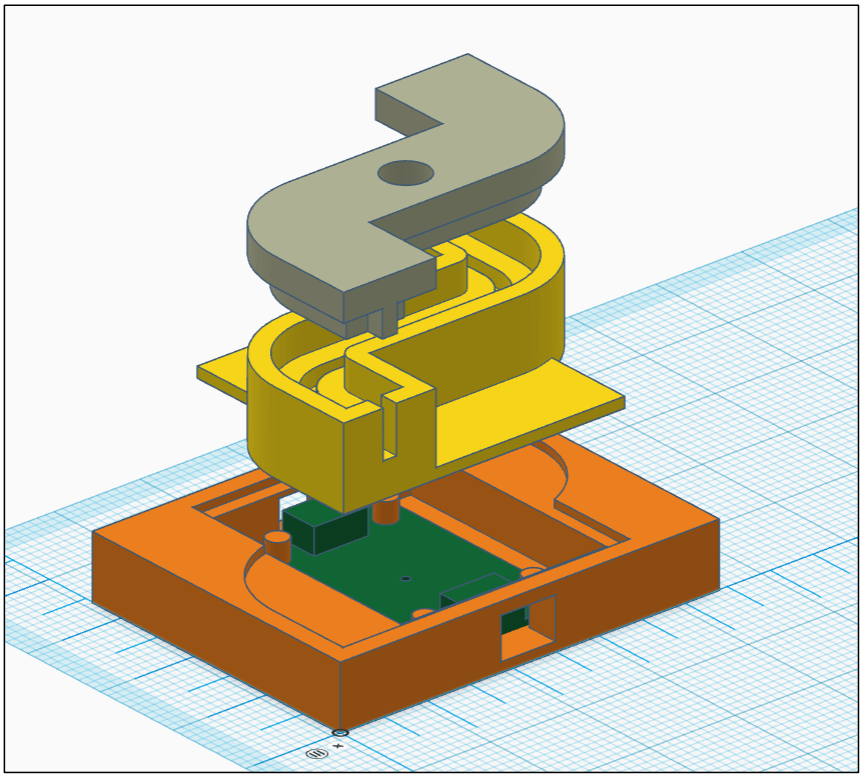
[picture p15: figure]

Figure S7 - Exploded CAD view of prototype detector module

Once initial success was confirmed and we moved to the finalised circuit, with custom circuit board and RJ45 link between the Raspberry Pi and detector module we designed a larger detector module housing incorporating the RJ45 connector and an access hole through which the LED wires could be fed (Figure S8, Figure S9).

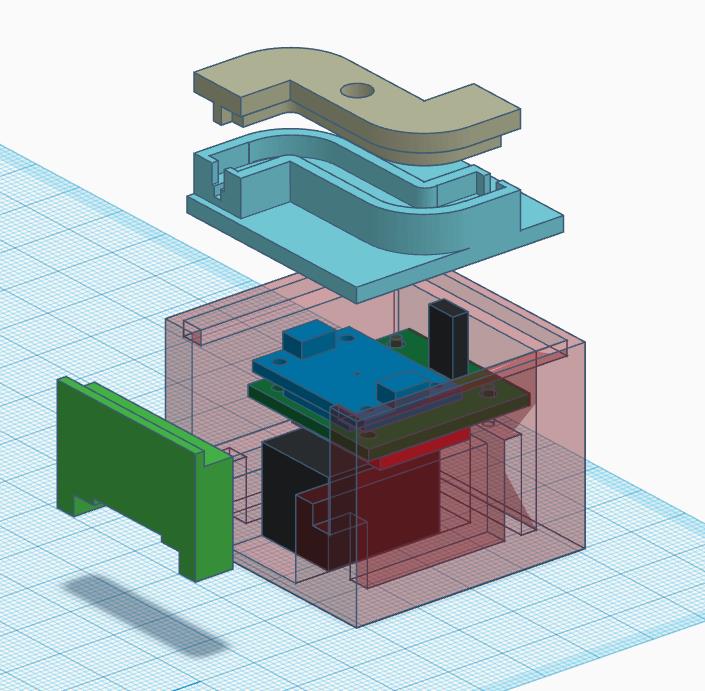
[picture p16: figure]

Figure S8 - Exploded CAD view of finalised detector module

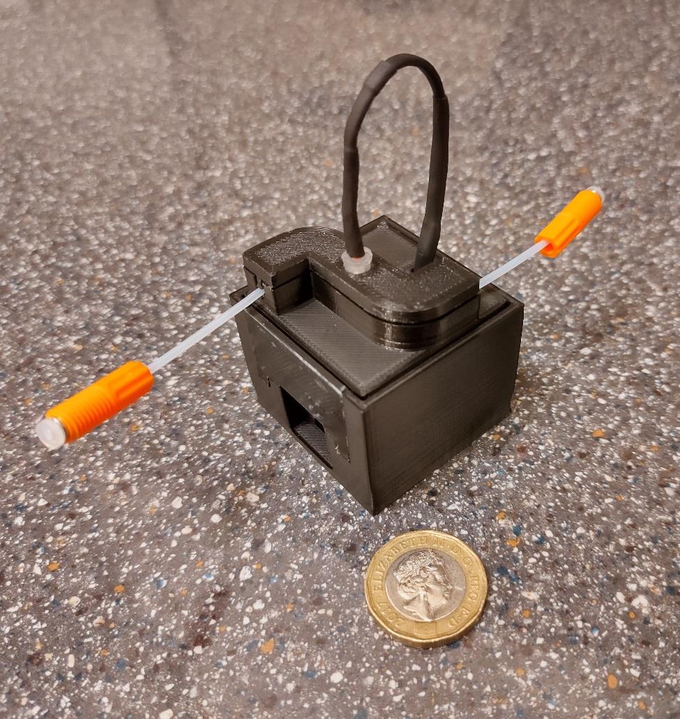
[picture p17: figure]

Figure S9 - 3D printed and fully constructed detector module

### S4.2 - Raspberry Pi Case Design

The starting point for the Raspberry Pi case design was the snap-fit design published by Malolo on the Thingiverse. [4]

The inclusion of the RJ45 connector on the custom HAT board resulted in a vertical height greater than is standard for Raspberry Pi devices. As a result, a small cut-out was made in the top surface of the case to allow the connector to stand proud. A small additional cap was then made to insert into the slot created – ensuring the RJ45 port was still protected.

In addition to this modification, to the top surface of the Pi case (and cap) was added a stippled pattern. This was for aesthetic reasons, to overcome the inconsistent patternation caused by the print bed (the case and cap are printed upside down relative to their intended orientation during use).

A further minor addition to the Malolo design was the inclusion of 4 feet to raise the bottom of the case off the fume hood floor – improving airflow, processor heat dissipation and protection from spilt solvent.

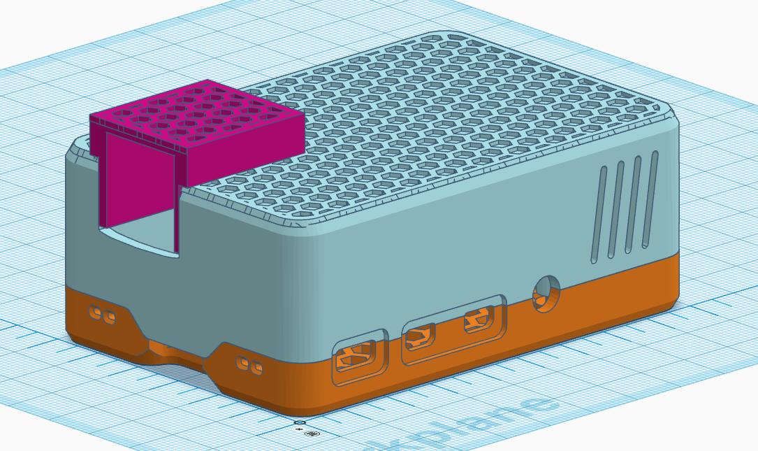
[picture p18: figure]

Figure S10 - Pi case CAD view: the base in orange, top in blue and RJ45 cap in pink. Feet are not shown.

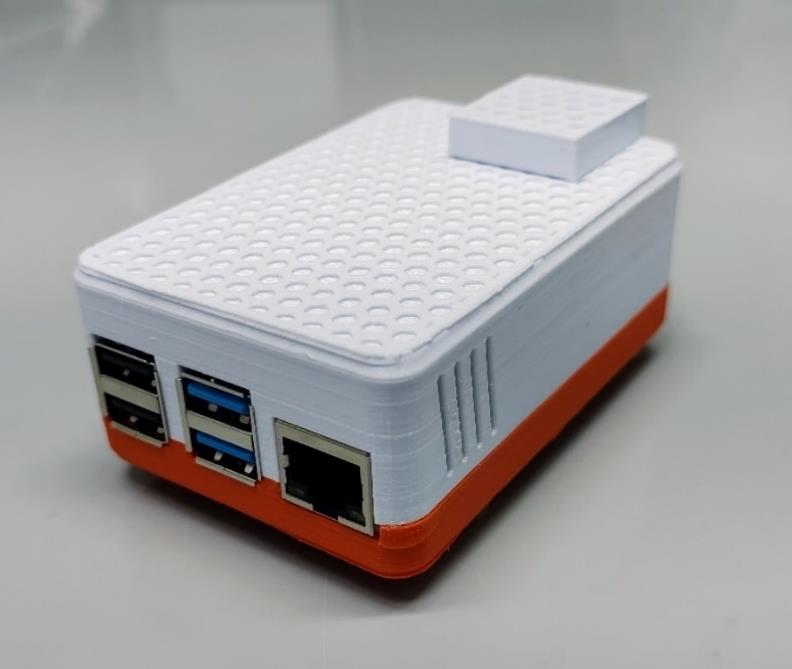
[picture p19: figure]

Figure S11 - Constructed Pi case

### S4.3 - STL File Availability

All .stl files for the finalised design are available from our GitHub page -https://github.com/vernalis/digital-lab/tree/main/Inline%20Detector/3D%20Printed%20Parts

See S4.4 for optimal printing settings and S5.2 & S5.4 for assembly instructions.

### S4.4 - 3D Printing Settings

All components were 3D printed using an Ultimaker S5, using 2.85mm filament.

The Raspberry Pi case was printed in polyethylene terephthalate glycol (PETG) due its higher tolerance to temperature – preventing any warping during use due to heat coming from the Pi’s processor.

The Pi case feet were printed in polypropylene (PP) due to its higher solvent resistance.

The detector module had no material requirements (other than being opaque), therefore polylactic acid (PLA) was used.

When printing interlocking parts (e.g. the fluidic pipe guide) these should be printed in the same orientation as each other on the print bed to minimise any printer tolerance issues in the x and y planes.

| Material
Condition | Polypropylene | PLA | PETG
Settings
Print core temperature (°C) | 240 | 200 | 245
Build plate temperature (°C) | 85 | 60 | 85
Print speed (mm/s) | 25 | 70 | 60
Fan speed (%) | 20 | 20 | 20
Print quality
Layer height (mm) | 0.1 | 0.15 | 0.15
Wall thickness (mm) | 1.14 | 1 | 1.3
Top/bottom thickness (mm) | 1 | 1 | 1.2
Infill density (%) | 100 | 20 | 20
Infill pattern | Octet | Triangles | Triangles
Build plate adhesion
Prime blob | Enabled | Enabled | Enabled
Adhesion type | Brim | Brim | Brim
Plate adhesion sheet | PP | None | None
Table S2 - 3D printer settings

## S5 - Assembly of Devices

### S5.1 - Assembly of Detector Module Circuit Board

1. Remove excess perimeter from the supplied detector circuit board (see Figure S6). File off any remaining burrs.
2. Solder supplied header pins to Adafruit AS7341 breakout board. (Solder from the top face of the board, black plastic, and majority of the pin, therefore below the board).
3. Fit the AS7341 board to the top face of the detector board (silkscreen markings allow easy identification of component location) with the pins going through the holes provided. Solder the sensor in place, soldering from the bottom face of the detector board.
4. Using two header pins, solder a positive (e.g. red) and negative (e.g. black) wire to power the LED from the top face of the detector board. (Figure S12)

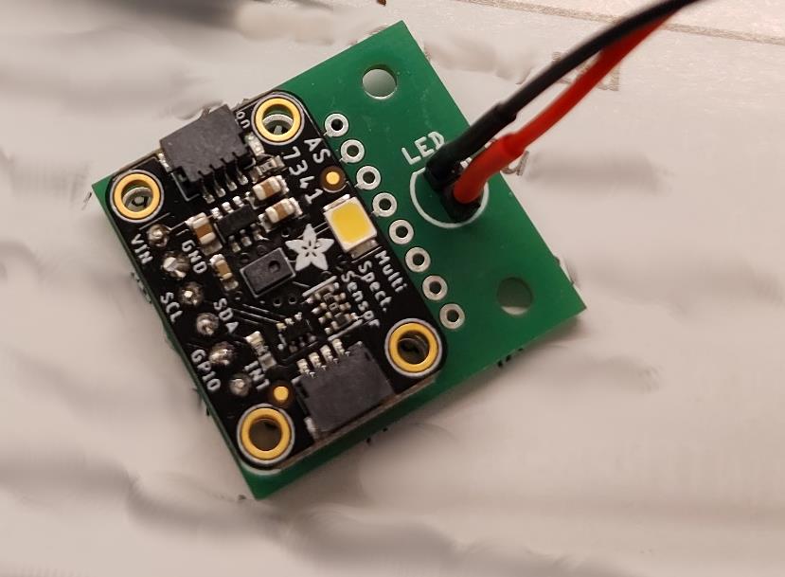
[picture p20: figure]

Figure S12 - AS7341 and LED wires connected to top face of detector board

5. Secure the soldered wire connections with heat shrink wrap.
6. Encase the two LED wires in a further heat shrink wrap (to create one thicker ‘wire’). NOTE: do not attach the LED, or shrink the outer wrap with heat yet!
7. Push the two RJ45 parts together (the connector and the breakout board) – the two locating pegs should click into position.
8. Solder the 8 connector pins to the breakout board.

9. Attach and solder 8 header pins to the underside of the RJ45 breakout board. (Figure S13)

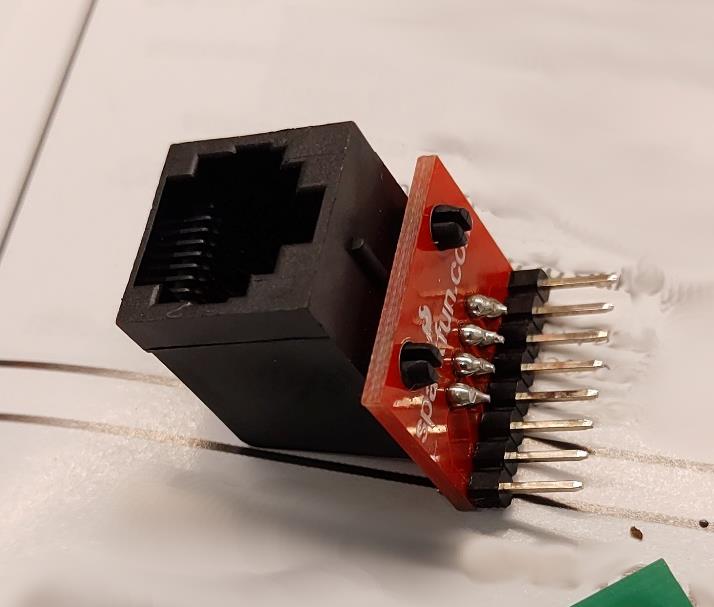
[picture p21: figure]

Figure S13 - Completed RJ45 breakout board

10. Fit the RJ45 breakout board to the underside of the detector board and solder in place from the top face. Detector module circuit board is now complete. (Figure S14)

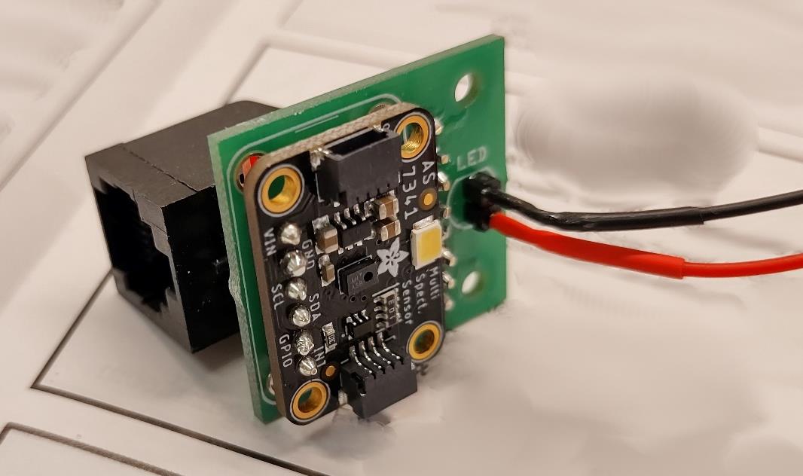
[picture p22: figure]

Figure S14 - Completed detector module circuit board

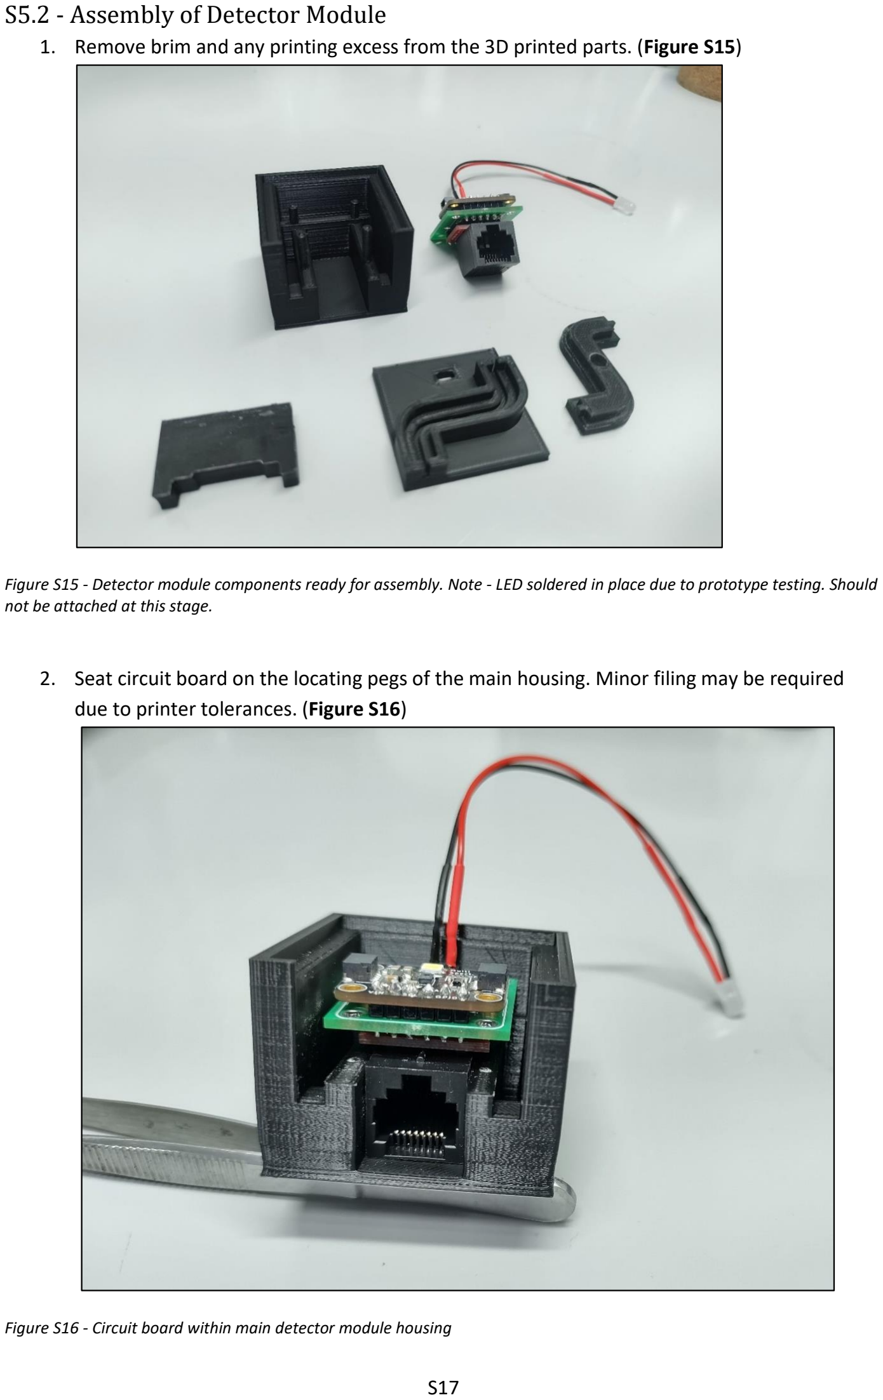
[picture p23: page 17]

### S5.2 - Assembly of Detector Module

1. Remove brim and any printing excess from the 3D printed parts. (Figure S15)

Figure S15 - Detector module components ready for assembly. Note - LED soldered in place due to prototype testing. Should not be attached at this stage.

2. Seat circuit board on the locating pegs of the main housing. Minor filing may be required due to printer tolerances. (Figure S16)

Figure S16 - Circuit board within main detector module housing

3. Fit the RJ45 cover to the wall of the detector module left open in Figure S16.
4. Fit a short length (approx. 15cm) of 1/16th od PTFE tubing into the pipe guide. Minor filing is likely required due to the tight tolerance (particularly at the bends). Use a smooth tool to push the tubing firmly into the channel without damaging the pipe’s surface. Fit two ¼-28” fluidic connections to the pipe, allowing easy connection to a fluidic system.
5. Thread the two LED wires through the hole included in the pipe guide.
6. Solder a white LED to the other ends of the LED wires. The longer leg is the anode, therefore should be attached to the positive (red) wire. Again, protect the soldered joints with heat shrink wrap. Then heat the outer heat shrink layer, creating one single wire.
7. Push the LED into the LED top plate from the top side. This should be a tight fit, but may need minor filing depending on printer tolerances. Detector module is now complete. (Figure S17)

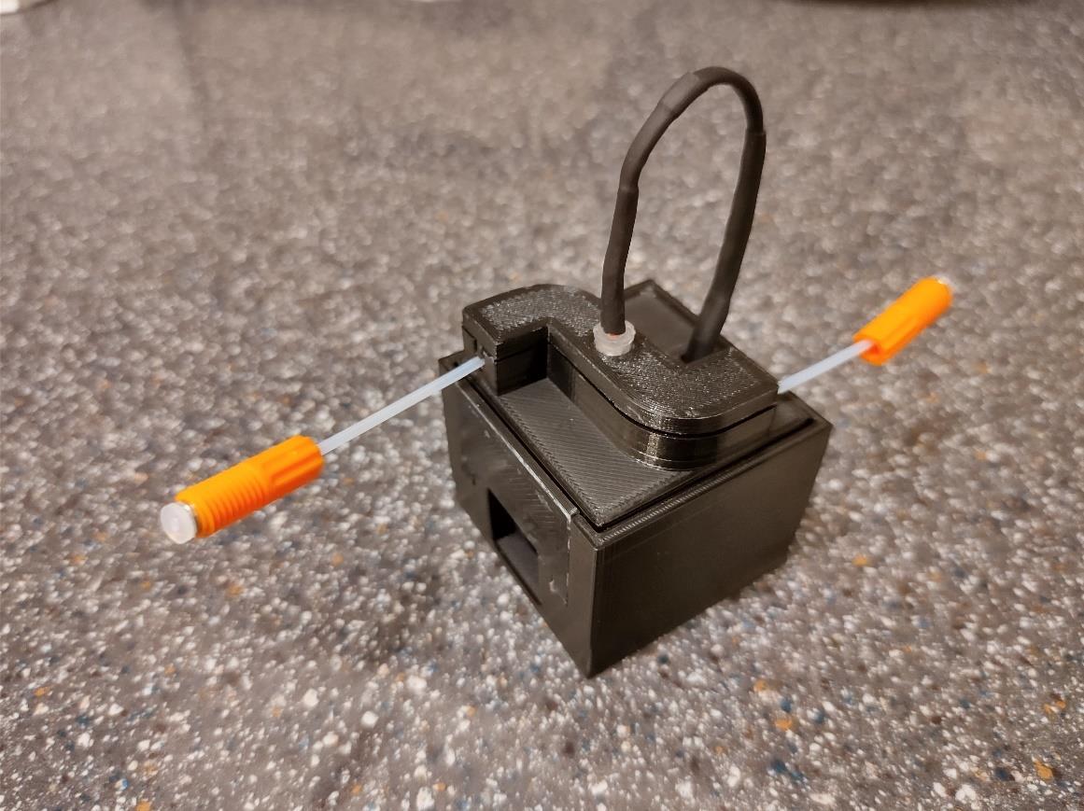
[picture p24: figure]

Figure S17 - Completed detector module

### S5.3 - Assembly of HAT Circuit Board

1. Fit a female GPIO socket header to the underside of the HAT circuit board. Secure in place by soldering from the top face of the HAT.
2. Fit two 10 kΩ and one 1 kΩ resistors to the top face of the HAT using the indicated holes. Solder in place from the underside.
3. Fit the NPN transistor (PN2222) to the top face of the HAT using the indicated holes. Note the curved face matches the silkscreen markings on the board (i.e. flat face is nearest the RJ45 connector). Solder in place from the underside.
4. Construct the second RJ45 breakout board, following steps 7-9 from the detector module circuit board assembly instructions (S5.1).
5. Fit the RJ45 breakout board to the top face of the HAT using the indicated holes. Solder in place from the underside. HAT circuit board is now complete. (Figure S18)


Figure S18 - Completed HAT board

### S5.4 - Assembly of Raspberry Pi Module

1. Insert 32Gb SD card into Raspberry Pi
2. Attach HAT board to the GPIO pins using the female socket soldered to the bottom side of the board.
3. Remove brim and any printing excess from the 3D printed parts.
4. Attach the four poly propylene feet to the underside of the Pi case using UHU ENDFEST 300 epoxy resin.

[5]
5. Carefully fit Raspberry Pi to the base part of the Pi case. Some minor filing may be required due to printer tolerances, particularly around the USB, HDMI ports on the side of the case.
6. Round off with a file the corner of the HAT between the GPIO header and the additional RJ45 port (the outermost corner of the HAT board). This is to remove any clash with the tight, curved corner of the upper part of the case.
7. Slide the top part of the Pi case into position, carefully fitting the RJ45 port on the HAT through the opening provided. The upper and lower parts of the case should click together.
8. Fit the RJ45 cap to the top part of the case to protect the RJ45 port. Minor filing may be required to accommodate printer and assembly tolerances.
9. Use a LAN cable to connect the Pi to the detector module. Assembly is complete. (Figure S19)


Figure S19 - Completely assembled inline detector

## S6 - Raspberry Pi Configuration and Operation

### S6.1 - Configuring Raspberry Pi for Use

1. Download Raspberry Pi Imager (V1.7.3 used) from https://www.raspberrypi.com/software/
2. Select to install a Raspberry Pi OS (32-bit) with Raspberry Pi Desktop image (2022-09-22 release used, approx. 0.9GB)
3. Set the destination to the MicroSD card to be used in the Raspberry Pi
4. Click the gear icon to set advanced options as follows:
a. Custom hostname (note this down – you will need it later)
b. Enable SSH
c. Set a username and password (these will also be required later)
d. Enter your chosen WiFi SSID and enter the password for the network
5. Write the image to the MicroSD card
6. Once complete, insert the card into the Raspberry Pi and power it up
7. Connect to the Raspberry Pi via SSH, for example using Windows PowerShell, entering the following command (where username and hostname are replaced by those set in step 4):

ssh username@hostname

8. Approve the request (i.e type yes), and then enter your password
9. Enable VNC on the Raspberry Pi using this guide https://www.pitunnel.com/doc/access-vncremote-desktop-raspberry-pi-over-internet (https://www.pitunnel.com/doc/access-vnc-remote-desktop-raspberry-pi-over-internet)
10. Continue to follow the guide to install and configure VNC Viewer on your computer. There is no need to continue onto the “Creating a tunnel to access VNC remotely” step
11. Through the SSH window, enter the command:

sudo raspi-config

12. Select option 2 (display options) and then D5 (VNC resolution)
13. Set the display resolution to match the screen you will view the Pi through, for example 1920x1080. This enables a clear view of the entire graph within the VNC Viewer window
14. Exit the configuration tool and restart the Pi – the next time VNC is used the new larger screen resolution will be used
15. Using the Raspberry Pi, through VNC open the terminal (a black box with white “>_”)
16. Download the configuration script from our GitHub repository using the following command as one continuous line (too long to show as one line here):

wget https://raw.githubusercontent.com/vernalis/digital-lab/main/Inline%20Detector/Code/setup-script.sh

17. Change the execute permissions on the script with the command:

chmod u+x setup-script.sh

18. Run the configuration script (installing all required libraries and the inline detector code itself) with the command:

./setup-script.sh

19. Once this has completed (it may take some time on slower Raspberry Pi devices) at the reboot prompt, confirm the default (Y) option by pressing the return key
20. Once the Raspberry Pi has rebooted the device will be ready for regular operation, see the following section for operation.

### S6.2 - Inline Detector Operation

The inline detector was accessed via VNC to enable a graphical interface. Pumping of the system solvent was commenced before the inline detector code was initiated. To initiate the code, open the Raspberry Pi terminal and enter the command:

python inline_detector.py

This will initiate the code. Closing the graph window will begin the code shutdown procedure, generating a .png version of the graph. Experimental data will be stored in as a sub-folder “Data” within the directory from which the code is stored.

During execution of the code three initial sensor readings are taken to establish a baseline absorbance reading for the system solvent. Once the baseline has been established, new sensor readings are recorded approximately every 2.5 seconds. A graph plotting normalised absorbance values is re-rendered following each reading, with time on the x axis and relative absorbance on the y axis. Slugs can then be detected by observing of a change in absorbance (see Figure S22).

The raw absorbance values and the baseline-normalised absorbance values are saved in two separate .csv files for later reference if required. These files are regenerated every time a sensor reading is taken.

Upon completion of the flow experiment, the inline detector application should be terminated by closing the chart window. This will generate a .png image of the graph for later reference, switch off the LED and then terminate the code.

## S7 - Testing

### S7.1 - Initial Optimisation

The device was designed with the ability to control LED brightness, as a result two experiments were performed: one with LED brightness set to 50% and one at 100%. It was found 100% brightness gave the best signal to noise ratio and wasn’t too bright to obscure subtle changes in absorbance.

The sensor provides raw brightness values across a range of wavelengths, as a result the inherent absorbance of the system solvent is observed as a consistent non-zero value (Figure S20, A). To make identification of slugs easier, sensor values can be normalised by deduction of a mean absorbance value arising due to the carrier solvent. This results in an approximately zero value when there is just system solvent passing the detector (baseline), and either a positive or negative peak visible (dependent on the differing absorbance characteristics) when a slug is passing the detector (Figure S20, B).

Figure S20 demonstrates how normalisation of the sensor values makes slug detection much easier.


The supplied code therefore operates under these optimal conditions – 100% LED brightness, with normalised values plotted on the graph.

Figure S20 - Comparison of data representation without (A) and with (B) sensor value normalisation against THF system solvent baseline

### S7.2 - Validation of Detector

Once optimal detector settings were determined and the design was finalised a validation experiment was performed by incorporating the sensor into a Syrris Asia flow chemistry system.

A simple fluidic system (Figure S21) was configured with both Syrris Asia AutoRIM injectors on the same single channel, this was to enable a swift experiment with rapid sequential injections. By having two injection loops on one reaction channel one injection loop could be washing and refilling whilst the other was injecting into the reactor stream. The injected slugs (2ml) then passed the detector at a flow rate of 1ml/min before exiting the fluidic system, via a Back Pressure Regulator, BPR, set to 2 bar.


For the validation experiment THF was chosen because it is a typical solvent used within our system. Three different solutions were then injected as slugs: a dilute solution of iodine in THF, this coloured solution should be easily detectable; neat IPA (isopropyl alcohol) and finally neat ethyl acetate these were both chosen as they are colourless liquids and would be difficult to discern from THF by eye.

The resulting data output from the validation experiment is shown in Figure S22. All three slugs can be seen clearly, indicating that the detector works well – even for colourless solutions in a colourless carrier solvent stream.

The sharp negative spike before the iodine and IPA slugs is due to the Syrris Asia AutoRIM. To ensure a sharp slug/system solvent interface a small nitrogen bubble at the system pressure is introduced at either end of the slug. The nitrogen bubble has its own unique absorbance profile. It is not clear why the bubble wasn’t observed for the ethyl acetate slug. A bubble was not introduced at the back of the slug in this experiment because slug timing was operated by manual control, and the injection was halted before the nitrogen bubble had exited the injection loop.

Figure S21 - Fluidic scheme for detector validation experiment


Figure S22 - Results of validation experiment. Colourless IPA and ethyl acetate slugs are clearly visible against colourless THF carrier solvent

## S8 - References

[1] https://www.petervis.com/Raspberry_PI/Driving_LEDs_with_CMOS_and_TTL_Outputs/Driving_an_LED_Using_Transistors.html (https://www.petervis.com/Raspberry_PI/Driving_LEDs_with_CMOS_and_TTL_Outputs/Driving_an_LED_Using_Transistors.html)
[2] https://circuitdigest.com/microcontroller-projects/raspberry-pi-pwm-tutorial
[3] Höving, S., Bobers, J. & Kockmann, N. Open-source multi-purpose sensor for measurements in continuous capillary flow. J Flow Chem 12, 185–196 (2022) https://doi.org/10.1007/s41981-021-00214-w
[4] https://www.thingiverse.com/thing:3723561
[5] https://www.uhu.com/en/product-page.63251
[6] https://learn.adafruit.com/circuitpython-on-raspberrypi-linux/installing-circuitpython-onraspberry-pi (https://learn.adafruit.com/circuitpython-on-raspberrypi-linux/installing-circuitpython-on-raspberry-pi)

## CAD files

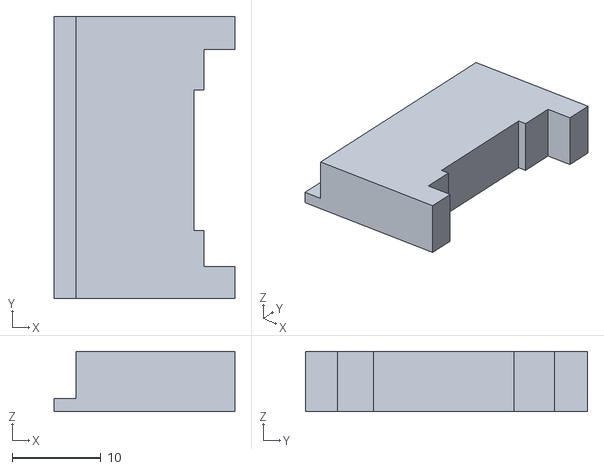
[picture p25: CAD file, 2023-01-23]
Inline Detector/3D Printed Parts/Detector/RJ45 Cover.stl
20.4 x 31.8 x 6.80

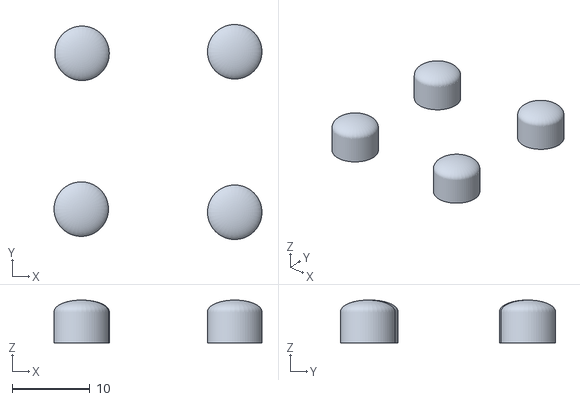
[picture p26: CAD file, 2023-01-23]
Inline Detector/3D Printed Parts/Pi Case/Feet.stl
26.7 x 27.6 x 5.50

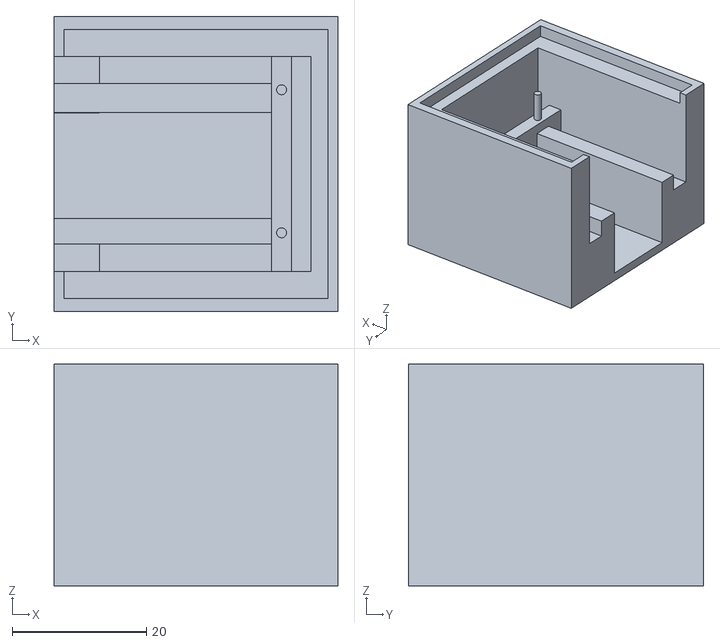
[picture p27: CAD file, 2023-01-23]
Inline Detector/3D Printed Parts/Detector/Circuit Housing.stl
42.3 x 44.0 x 33.0

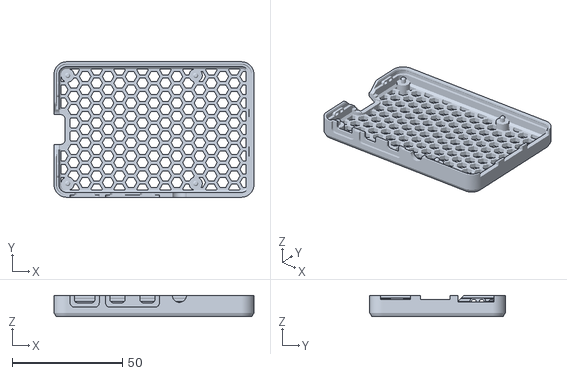
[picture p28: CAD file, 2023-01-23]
Inline Detector/3D Printed Parts/Pi Case/Base.stl
90.6 x 61.4 x 9.70

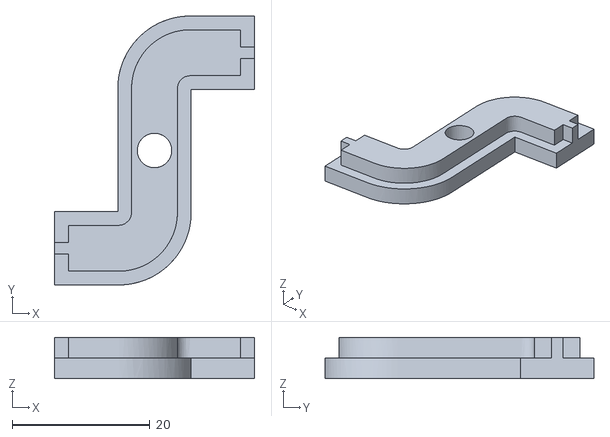
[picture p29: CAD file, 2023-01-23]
Inline Detector/3D Printed Parts/Detector/LED Top Plate.stl
29.0 x 39.0 x 6.00

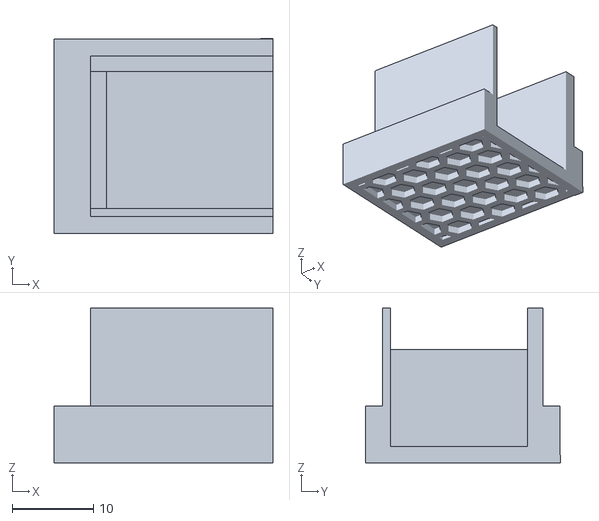
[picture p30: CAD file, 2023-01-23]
Inline Detector/3D Printed Parts/Pi Case/RJ45 Cap.stl
27.0 x 24.1 x 19.1

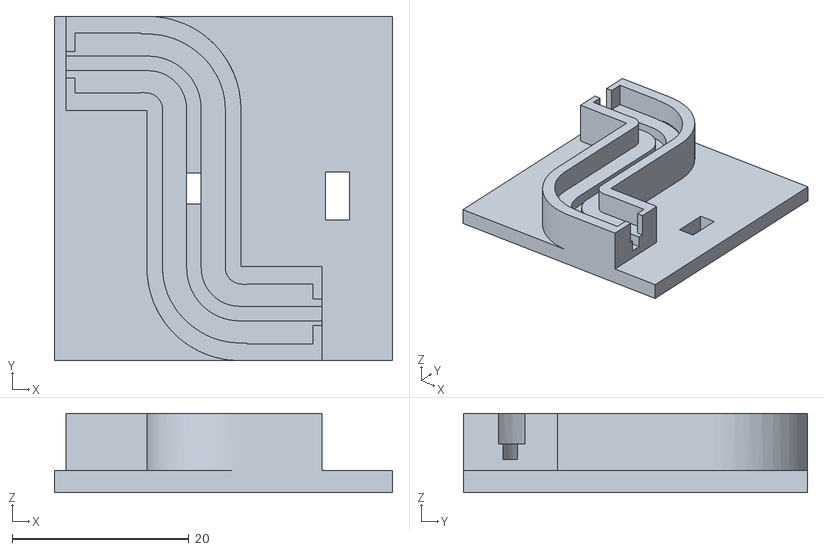
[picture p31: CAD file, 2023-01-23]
Inline Detector/3D Printed Parts/Detector/Pipe Guide.stl
38.3 x 39.0 x 9.00

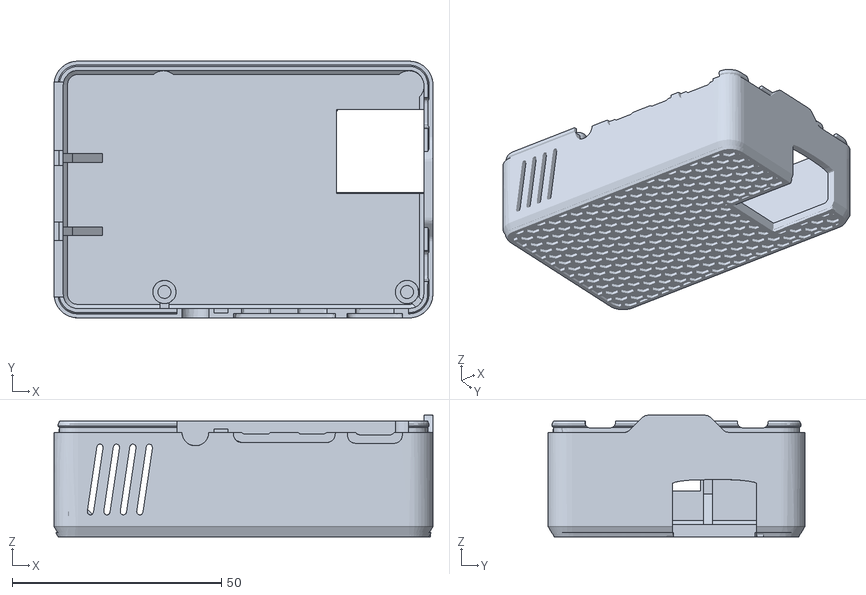
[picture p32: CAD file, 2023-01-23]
Inline Detector/3D Printed Parts/Pi Case/Top.stl
90.6 x 61.4 x 29.1

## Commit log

2021-10-29 Upload Circuit Diagram
2021-10-29 Replace Circuit.png for higher resolution
2021-10-30 Use snake case not camel case for variables
2023-01-23 V1.1 HAT PCB (add compatibility for Pi Zero)
2023-01-24 Add setup script for Raspberry Pi

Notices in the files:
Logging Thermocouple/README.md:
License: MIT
